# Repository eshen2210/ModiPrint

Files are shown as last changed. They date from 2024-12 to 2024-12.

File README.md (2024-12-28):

# ModiPrint-Desktop

## Introduction

ModiPrint is a powerful, modular, feature-rich open-source 3D bioprinter.


**High resolution Hydrogel Extrusion** 
100 micron alginate filaments (500 micron scale bars).


**Multi-Material prints** 
Printheads mounted on independent Z-actuators enable multiple materials in one print.


**CAD Integration** 
Integration with g-code allows complex 3D models to be fully realized in print.


**Gentle** 
Human induced pluripotent stem cells remained viable for 30 days after print.


**Concentration Gradients** 
Integration of extrusion and inkjet printing embeds small molecule gradients of into hydrogels of any geometry.


## User Guide

This is the complete guide to building and operating ModiPrint. Construction and operation of this 
bioprinter requires the user to: 
1. Acquire all hardware via vendors. 
2. Assemble the hardware using this guide.
3. Install the open-source desktop and microcontroller software. 

Please see the [User Guide](https://github.com/eshen2210/ModiPrint/blob/main/User%20Guide.pdf) for full instructions.

See the [peer-reviewed scientific publication of ModiPrint](https://www.sciencedirect.com/science/article/pii/S2405886620300403).

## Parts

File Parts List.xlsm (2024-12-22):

 |  |  |  | Parts Total (Not Including Tools and Consumables) |  |  |  | Tools |  |  |  | Consumables
 |  |  |  |  | Quantity
Number of Pneumatic Extruders | 1 |  |  | Part Name | (Rounded) | Price ($) Per Unit | Comments | Part Name | Comments |  |  | Part Name | Quantity | Price ($) Per Unit | Comments
 |  |  |  | 062 MINSTAC Adapter – 125/156 MINSTAC | 1 | $52.26 | The Lee Company Quote #TMDA3203950Z – PEEK | Metric Hex Wrenches | For most of the Openbuilds parts. |  |  | 3 cc Syringe Barrels (50 Pack) |  | $30.61 | Nordson EFD Quote #7012072
Number of Microdispensing Inkjets | 1 |  |  | 062 MINSTAC Male – 062 MINSTAC Male | 1 | $12.00 | The Lee Company Quote #TMUA3205950Z – PEEK | Heat Gun (https://www.amazon.com/Genesis-GHG1500A-Temperature-Nozzle-Attachments/dp/B00EU2T8GG) | For the heat shrink. |  |  | 3cc Syringe Barrel Piston (50 Pack) |  | $29.14 | Nordson EFD Quote #7014602
 |  |  |  | 1/4" x 8mm Flexible Coupling | 3 | $6.99 |  | Flat Head Screwdriver |  |  |  | Nordson EFD Tips (https://azcscxpprodcdn.azureedge.net/-/media/Files/Nordson/efd/Products/Data-Sheets/Components/EN_Nordson_EFD_Optimum_Brochure.pdf?la=en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)
 |  |  |  | 10-32 UNF Plug (SPG-10-1/4) (25 Pack) (https://www.pneumadyne.com/plug-fittings-p-2173.html?cPath=135_153_160&ref_id=2178) | 1 | $14.50 |  | Soldering Iron & Solder (https://www.amazon.com/Soldering-Iron-Kit-Temperature-Rarlight/dp/B07PDK3MX1) | For soldering spliced wires. |  |  | Replacement O-Rings for Nordson EFD Adapters (10 Pack) |  | $6.34 | Nordson EFD Quote #7018502
Press Ctrl + Alt + F9 to refresh all part totals after changing printhead counts. |  |  |  | 12 Gauge Wire (https://www.amazon.com/BNTECHGO-Silicone-Flexible-Strands-Stranded/dp/B01ABOPMEI) | 1 | $12.98 |  | Wire Stripper (https://www.amazon.com/Seikotools-Stripper-Yellow-Black-Stripping-Multi-Function/dp/B07KF7D51T) | For splicing wires. |  |  | Replacement O-Rings for Quick Disconnect Fittings (100 Pack) |  | $64.24 | Cole-Parmer Quote #00080XG
Decimal part amounts indicate that only partial packs of parts will be used. |  |  |  | 125/156 MINSTAC – Female Tube – Luer Adapter | 1 | $76.85 | The Lee Company Quote #TMRA9502950Z – PEEK | Power Tool (https://www.amazon.com/BLACK-DECKER-BDCD8C-Lithium-Drill/dp/B0111N8O6G) | For self-tapping screws and to widening the mini gantry plate hole
The "Parts Total" section sums all parts required to build a printer with the specified number of printheads. |  |  |  | 15x20mm Drag Chain (https://www.amazon.com/gp/product/B075FCG31X/ref=ppx_yo_dt_b_search_asin_title?ie=UTF8&psc=1) | 4 | $14.00 |  | 5mm Drill Bit (https://www.amazon.com/Silverline-Cobalt-Drill-Bits-5-0mm/dp/B000LFY1HW) | For widening the mini gantry plate hole
Please report any mistakes to eshen2210@gmail.com |  |  |  | 2 Hole Joining Strip Plate (https://openbuildspartstore.com/2-hole-joining-strip-plate/) | 3 | $1.99 |  | Screw Extractor (https://www.amazon.com/Extractor-Stripped-HassleFree-Hardness-63-65hrc/dp/B07GZ17QD9) | In case the aluminum screws are stripped
Total Cost | $3123.67 |  |  | 24 Gauge Wire (https://www.amazon.com/gp/product/B01KQ0D3M0) | 3 | $14.99 | The quantity here is an estimate.
 |  |  |  | 24V 1A Power Supply (https://www.amazon.com/Signcomplex-Transformers-Switching-Household-Electronics/dp/B0797MW8J6) | 1 | $14.99 | Only necessary if you are using pneumatic extruders.
 |  |  |  | 3 Hole Joining Strip Plate (https://openbuildspartstore.com/3-hole-joining-strip-plate/) | 23 | $1.99
 |  |  |  | 3/16 Barb to 1/4 NPT (25 Pack) (https://www.pneumadyne.com/316-tube-barb-straight-connectors-npt-p-1899.html?cPath=135_136_137_144) | 1 | $7.70
 |  |  |  | 3/16 Barb to 1/8 NPT (EB-1/8) (25 Pack) (https://www.pneumadyne.com/316-tube-barb-straight-connectors-npt-p-1857.html?cPath=135_136_137_142) | 1 | $39.50
 |  |  |  | 3/16 Barb to 10-32 UNF (25 Pack) (https://www.pneumadyne.com/316-tube-barb-straight-connectors-unf-p-1803.html?cPath=135_136_137_138) | 1 | $15.00
 |  |  |  | 3/16'' ID Barb to 1/8'' NPT Female (https://www.amazon.com/Parker-Hannifin-Par-Barb-Connector-Fitting/dp/B01BYLM3T4) | 1 | $10.54
 |  |  |  | 3/16'' ID Quick Disconnect Female (https://www.coleparmer.com/i/cpc-colder-pmcd1703-hose-barb-fitting-body-valved-3-16-tube-id-1-8-flow-size-acetal/0636022) | 2 | $9.90
 |  |  |  | 3/16'' ID Quick Disconnect Male (https://www.coleparmer.com/i/cpc-colder-pmc2203-hose-barb-insert-straight-through-3-16-tube-id-1-8-flow-size-acetal/0636044) | 1 | $3.10
 |  |  |  | 3/16'' ID Tee Connector (10 Pack) (https://www.coleparmer.com/i/cole-parmer-barbed-tee-connector-polyethylene-3-16-10-pack/3062367) | 1 | $17.80
 |  |  |  | 3/16'' ID Tubing (https://www.amazon.com/ATP-Vinyl-Flex-Plastic-Tubing-Length/dp/B00E6BCXQ8) | 1 | $11.68
 |  |  |  | 3/2 Solenoid Valve (McMaster Carr 61975K244) (https://www.mcmaster.com/) | 1 | $58.90
 |  |  |  | 3cc Syringe barrel Adapter with Filter Trap | 1 | $33.22 | Nordson EFD Quote #7012063
 |  |  |  | 5mm * 8mm Flexible Coupling (https://openbuildspartstore.com/5mm-8mm-flexible-coupling/) | 2 | $6.99
 |  |  |  | 7-12V 1A Power Supply (https://www.amazon.com/IBERLS-Adapter-Arduino-Supply-Connectors/dp/B077ZPGQ1K) | 1 | $8.97
 |  |  |  | 8mm Metric Acme Lead Screw (290 mm) (https://openbuildspartstore.com/8mm-metric-acme-lead-screw/) | 2 | $10.99
 |  |  |  | 8mm Metric Acme Lead Screw (540 mm) (https://openbuildspartstore.com/8mm-metric-acme-lead-screw/) | 3 | $21.99
 |  |  |  | Aluminum Spacer (10 Pack) (1.5 inches) (https://openbuildspartstore.com/aluminum-spacers-10-pack/) | 1 | $6.49
 |  |  |  | Aluminum Spacers (10 Pack) (20 mm) (https://openbuildspartstore.com/aluminum-spacers-10-pack/) | 3 | $4.99
 |  |  |  | Aluminum Spacers (10 Pack) (3 mm) (https://openbuildspartstore.com/aluminum-spacers-10-pack/) | 2 | $2.49
 |  |  |  | Aluminum Spacers (10 Pack) (40 mm) (https://openbuildspartstore.com/aluminum-spacers-10-pack/) | 1 | $6.49
 |  |  |  | Aluminum Spacers (10 Pack) (6 mm) (https://openbuildspartstore.com/aluminum-spacers-10-pack/) | 4 | $2.99
 |  |  |  | Aluminum Spacers (10 Pack) (9 mm) (https://openbuildspartstore.com/aluminum-spacers-10-pack/) | 3 | $3.49
 |  |  |  | Anti-Backlash Nut Block for 8mm Metric Acme Lead Screw (https://openbuildspartstore.com/anti-backlash-nut-block-for-8mm-metric-acme-lead-screw/) | 8 | $9.99 | See the link for proper installation instructions.
 |  |  |  | Arduino MEGA (https://www.amazon.com/ELEGOO-ATmega2560-ATMEGA16U2-Projects-Compliant/dp/B01H4ZLZLQ) | 1 | $14.99
 |  |  |  | Ball Bearing 688Z 8x16x5 | 10 | $0.99
 |  |  |  | Black Angle Corner Connector (https://openbuildspartstore.com/black-angle-corner-connector/) | 28 | $2.99
 |  |  |  | Bottom Surface (440 x 500 mm) (https://www.lowes.com/pd/OPTIX-18-in-x-24-in-Clear-Acrylic-Sheet/3502292) | 1 | $26.48 | This is just a big surface for the electronics and has no real requirements. We use acrylic because it's sturdy and can be cut to order in many hardware stores.
 |  |  |  | Braided Cable 1/4'' (~20 ft) (https://www.amazon.com/gp/product/B01M3SG5P7) | 0 | $9.99
 |  |  |  | Button Head Screws M3 (10 Pack) (8mm) (https://openbuildspartstore.com/button-head-screws-m3-25-pack/) | 1 | $1.95
 |  |  |  | C-Beam® End Mount (https://openbuildspartstore.com/c-beam-end-mount/) | 6 | $8.99
 |  |  |  | C-Beam® Linear Rail (500 mm) (https://openbuildspartstore.com/c-beam-linear-rail/) | 3 | $14.99
 |  |  |  | Digital Pressure Gauge (1/8'' NPT) (https://www.amazon.com/Kodiak-Controls-KCDG154145-Pressure-0-145PSI/dp/B00H9ZWPY8) | 1 | $31.99
 |  |  |  | DQ542MA Stepper Motor Driver (https://openbuildspartstore.com/dq542ma-stepper-motor-driver/) | 5 | $39.99
 |  |  |  | Eccentric Spacer (6 mm) (https://openbuildspartstore.com/eccentric-spacer/) | 16 | $1.99 | See the link for proper installation instructions.
 |  |  |  | End Cap (http://openbuildspartstore.com/end-cap/) | 34 | $1.85
 |  |  |  | Heat Shrink (https://www.amazon.com/gp/product/B075WR9FVL) | 1 | $7.98
 |  |  |  | IRF520 MOSFET Driver (5 Pack) (https://www.amazon.com/HiLetgo-IRF520-MOSFET-Arduino-Raspberry/dp/B01I1J14MO/) | 1 | $5.99
 |  |  |  | L Bracket (Double) (http://openbuildspartstore.com/l-bracket/) | 8 | $1.49
 |  |  |  | L Bracket (Single) (https://openbuildspartstore.com/l-bracket/) | 1 | $1.29
 |  |  |  | LM2596 Adjustable Converter (https://www.amazon.com/gp/product/B074XRYC1M/) | 1 | $9.99
 |  |  |  | Lock Collar (https://openbuildspartstore.com/lock-collar/) | 10 | $0.99
 |  |  |  | Low Profile Screws M5 (10 Pack) (10 mm) (https://openbuildspartstore.com/low-profile-screws-m5-10-pack/) | 3 | $1.49
 |  |  |  | Low Profile Screws M5 (10 Pack) (12 mm) (https://openbuildspartstore.com/low-profile-screws-m5-10-pack/) | 1 | $1.49
 |  |  |  | Low Profile Screws M5 (10 Pack) (15 mm) (https://openbuildspartstore.com/low-profile-screws-m5-10-pack/) | 1 | $1.59
 |  |  |  | Low Profile Screws M5 (10 Pack) (20 mm) (https://openbuildspartstore.com/low-profile-screws-m5-10-pack/) | 4 | $1.69
 |  |  |  | Low Profile Screws M5 (10 Pack) (25 mm) (https://openbuildspartstore.com/low-profile-screws-m5-10-pack/) | 1 | $1.79
 |  |  |  | Low Profile Screws M5 (10 Pack) (30 mm) (https://openbuildspartstore.com/low-profile-screws-m5-10-pack/) | 1 | $1.89
 |  |  |  | Low Profile Screws M5 (10 Pack) (35 mm) (https://openbuildspartstore.com/low-profile-screws-m5-10-pack/) | 1 | $1.99
 |  |  |  | Low Profile Screws M5 (10 Pack) (45 mm) (https://openbuildspartstore.com/low-profile-screws-m5-10-pack/) | 1 | $2.19
 |  |  |  | Low Profile Screws M5 (10 Pack) (55 mm) (https://openbuildspartstore.com/low-profile-screws-m5-10-pack/) | 1 | $2.39
 |  |  |  | Low Profile Screws M5 (10 Pack) (60 mm) (https://openbuildspartstore.com/low-profile-screws-m5-10-pack/) | 2 | $2.49
 |  |  |  | Low Profile Screws M5 (10 Pack) (8 mm) (https://openbuildspartstore.com/low-profile-screws-m5-10-pack/) | 9 | $1.39
 |  |  |  | M3 30 mm Screw (20 Pack) (https://www.amazon.com/gp/product/B07DDG19KG) | 1 | $7.99
 |  |  |  | M3 3mm Female Hex Thread Metal Nut (https://www.amazon.com/100Pcs-Female-Thread-Fastener-Silver/dp/B00GYS1SXU) | 1 | $3.69
 |  |  |  | M3 60mm Hex Socket Head Screw (60 Pack) (https://www.amazon.com/Stainless-Steel-Phillips-Screws-60pcs/dp/B012TE19QS) | 1 | $13.59
 |  |  |  | M3 Drop-In Tee Nuts (https://www.amazon.com/CNBTR-10x6x4mm-Aluminum-European-HeadDrop/dp/B01D83GZ7C) | 1 | $7.50
 |  |  |  | M5 1mm Washer (100 Pack) (https://www.amazon.com/Steel-Washer-Plated-Finish-Metric/dp/B009OK4TZO?s=gateway) | 1 | $3.21
 |  |  |  | M5 Drop-In Tee Nuts (https://www.amazon.com/100Pcs-T-Nuts-Carbon-Nickel-Plated-Sliding/dp/B07KSFB7BG?s=gateway) | 1 | $9.99
 |  |  |  | Meanwell LRS-350-24 Power Supply (https://www.amazon.com/MeanWell-LRS-350-24-Power-Supply-350W/dp/B077B36KPB) | 1 | $33.25
 |  |  |  | Micro Limit Switch Kit (https://openbuildspartstore.com/micro-limit-switch-kit/) | 10 | $4.99 | Determines the range limits of the actuator. The location of installation in the Sketchup file is only approximate. Adjust your own limit switch position to tune how far you want your actuator to travel.
 |  |  |  | Microdispensing Valve | 1 | $275.65 | The Lee Company Quote #INKX0507900A
 |  |  |  | Mini Pressure Regulator (McMaster Carr 9172K18) (https://www.mcmaster.com/) | 2 | $37.50
 |  |  |  | Mini V Gantry Plate (http://openbuildspartstore.com/mini-v-gantry-plate/) | 4 | $8.99
 |  |  |  | NEMA 23 Stepper Motor - High Torque Series (http://openbuildspartstore.com/nema-23-stepper-motor-high-torque-series/) | 3 | $39.95
 |  |  |  | Microdispensing Valve Nozzle | 1 | $44.92 | The Lee Company Quote #INZA6542460K
 |  |  |  | Nylon Insert Hex Locknut - M5 (10 Pack) (https://openbuildspartstore.com/nylon-insert-hex-locknut-m5-10-pack/) | 1 | $0.99
 |  |  |  | Pressure Regulator Mounting Bracket (McMaster Carr 9172K24) (https://www.mcmaster.com/9172k24) | 2 | $12.08
 |  |  |  | Pressure Splitter (M32-6) (https://www.pneumadyne.com/station-npt-input-aluminum-manifold-p-2601.html?cPath=193_194_199) | 2 | $10.95
 |  |  |  | Print Surface (440 x 500 mm) (https://www.lowes.com/pd/Gardner-Glass-Products-18-in-x-24-in-Clear-Glass/3121155) | 1 | $9.98 | This is your print surface and should be very stiff to not flex during operation. We use glass for the stiffness and aesthetics but it can be anything you want. You should be able find this stuff cut to order at your local hardware store. It's recommended that you tape off the edges if you decide to use glass.
 |  |  |  | Self Tapping Screw (http://openbuildspartstore.com/self-tapping-screw/) | 46 | $0.29
 |  |  |  | Shim - 12 x 8 x 1mm | 10 | $0.29
 |  |  |  | Slot Washer - 15x5x2mm (https://openbuildspartstore.com/slot-washer-15x5x2mm/) | 16 | $0.19
 |  |  |  | Socket Head Cap Screw M4 (https://openbuildspartstore.com/socket-head-cap-screw-m4/) | 2 | $0.09
 |  |  |  | Standard ROJ Power Cord (https://www.amazon.com/gp/product/B00I0VL96U) | 1 | $7.25
 |  |  |  | Stepper Motor - 68 oz. in (400 steps/rev) (https://www.sparkfun.com/products/10846) | 2 | $17.95
 |  |  |  | Surge Protector (https://www.amazon.com/AmazonBasics-6-Outlet-Protector-2-Pack-2-Foot/dp/B00TP1BWMK?s=gateway) | 1 | $8.45 | This is going to seem really jank, but I recommend securing this with some sturdy 2 sided tape. https://www.amazon.com/Double-Sided-Automotive-Mounting%EF%BC%8CWeatherproof-Decorative-Strip%EF%BC%8CPhoto/dp/B07K2RSJ8D?s=gateway
 |  |  |  | Tee Nuts - M5 (10 Pack) (https://openbuildspartstore.com/tee-nuts-m5-10-pack/) | 10 | $2.99 | See Drop In Tee Nuts as an easier to use alternative https://www.amazon.com/100Pcs-T-Nuts-Carbon-Nickel-Plated-Sliding/dp/B07KSFB7BG?s=gateway
 |  |  |  | Threaded Rod Plate - NEMA 17 Stepper Motor (http://openbuildspartstore.com/threaded-rod-plate-nema-17-stepper-motor/) | 4 | $6.99
 |  |  |  | Turn Key Hose Clamp 5/8'' to 1-1/4'' (10 Pack) (https://www.amazon.com/gp/product/B006IOZ2TG/ref=oh_aui_detailpage_o08_s00?ie=UTF8&psc=1) | 1 | $12.39
 |  |  |  | Vacuum Regulator (McMaster Carr 41585K43) (https://www.mcmaster.com/41585k43) | 1 | $56.70
 |  |  |  | Valve Driver | 1 | $174.80 | The Lee Company Quote #IECX0501350A
 |  |  |  | V-Slot Linear Rail 20mm x 20mm (250mm) (http://openbuildspartstore.com/v-slot-20x20-linear-rail/) | 2 | $3.29
 |  |  |  | V-Slot Linear Rail 20mm x 40mm (250mm) (http://openbuildspartstore.com/v-slot-20x40-linear-rail/) | 2 | $3.99
 |  |  |  | V-Slot® 20x20 Linear Rail (500 mm) (https://openbuildspartstore.com/v-slot-20x20-linear-rail/) | 4 | $5.49
 |  |  |  | V-Slot® 20x40 Linear Rail (250 mm) (https://openbuildspartstore.com/v-slot-20x40-linear-rail/) | 1 | $3.99
 |  |  |  | V-Slot® 20x40 Linear Rail (500 mm) (https://openbuildspartstore.com/v-slot-20x40-linear-rail/) | 2 | $6.99
 |  |  |  | V-Slot® 20x80 Linear Rail (250mm) (http://openbuildspartstore.com/v-slot-20x80-linear-rail/) | 3 | $5.99
 |  |  |  | V-Slot® 20x80 Linear Rail (500 mm) (https://openbuildspartstore.com/v-slot-20x80-linear-rail/) | 1 | $10.99
 |  |  |  | XLarge C-Beam Gantry Plate (https://openbuildspartstore.com/xlarge-c-beam-gantry-plate/) | 6 | $14.99
 |  |  |  | Xtreme Mini V Wheel Kit (https://openbuildspartstore.com/xtreme-mini-v-wheel-kit/) | 8 | $5.99
 |  |  |  | Xtreme Solid V Wheel Kit (https://openbuildspartstore.com/xtreme-solid-v-wheel-kit/) | 24 | $6.99 | Also comes with nuts and shims that will be used in conjunction with the wheel. A shim must be sandwiched in between 2 ball bearings within each wheel.
 |  |  |  | For Sterile Prints
 |  |  |  | Autoclavable 3/16'' ID Tubing (https://www.amazon.com/gp/product/B004VHJRCA) | 1 | $29.83
 |  |  |  | Autoclavable In-Line HEPA Filter (https://www.coleparmer.com/i/whatman-6723-5000-hepa-vent-filters-10pk-50mm-dia/2970090) | 1 | $122.00
 |  |  |  | Total |  | $3123.67
2 Y Actuators |  |  |  | Frame & Print Surface |  |  |  | Y Drag Chain & Outlet Extension |  |  |  | X Actuator
Part Name | Quantity | Price ($) Per Unit | Comments | Part Name | Quantity | Price ($) Per Unit | Comments | Part Name | Quantity | Price ($) Per Unit | Comments | Part Name | Quantity | Price ($) Per Unit | Comments
1/4" x 8mm Flexible Coupling | 2 | $6.99 |  | 2 Hole Joining Strip Plate (https://openbuildspartstore.com/2-hole-joining-strip-plate/) | 2 | $1.99 |  | 15x20mm Drag Chain (https://www.amazon.com/gp/product/B075FCG31X/ref=ppx_yo_dt_b_search_asin_title?ie=UTF8&psc=1) | 2 | $14.00 |  | 1/4" x 8mm Flexible Coupling | 1 | $6.99
3 Hole Joining Strip Plate (https://openbuildspartstore.com/3-hole-joining-strip-plate/) | 2 | $1.99 |  | 3 Hole Joining Strip Plate (https://openbuildspartstore.com/3-hole-joining-strip-plate/) | 6 | $1.99 |  | 3 Hole Joining Strip Plate (https://openbuildspartstore.com/3-hole-joining-strip-plate/) | 5 | $1.99 |  | 8mm Metric Acme Lead Screw (540 mm) (https://openbuildspartstore.com/8mm-metric-acme-lead-screw/) | 1 | $21.99
8mm Metric Acme Lead Screw (540 mm) (https://openbuildspartstore.com/8mm-metric-acme-lead-screw/) | 2 | $21.99 |  | Black Angle Corner Connector (https://openbuildspartstore.com/black-angle-corner-connector/) | 12 | $2.99 |  | Aluminum Spacers (10 Pack) (20 mm) (https://openbuildspartstore.com/aluminum-spacers-10-pack/) | 0.3 | $4.99 |  | Aluminum Spacers (10 Pack) (20 mm) (https://openbuildspartstore.com/aluminum-spacers-10-pack/) | 0.8 | $4.99
Aluminum Spacers (10 Pack) (20 mm) (https://openbuildspartstore.com/aluminum-spacers-10-pack/) | 0.8 | $4.99 |  | Bottom Surface (440 x 500 mm) (https://www.lowes.com/pd/OPTIX-18-in-x-24-in-Clear-Acrylic-Sheet/3502292) | 1 | $26.48 | This is just a big surface for the electronics and has no real requirements. We use acrylic because it's sturdy and can be cut to order in many hardware stores. | Aluminum Spacers (10 Pack) (6 mm) (https://openbuildspartstore.com/aluminum-spacers-10-pack/) | 0.1 | $2.99 |  | Aluminum Spacers (10 Pack) (3 mm) (https://openbuildspartstore.com/aluminum-spacers-10-pack/) | 0.4 | $2.49
Aluminum Spacers (10 Pack) (3 mm) (https://openbuildspartstore.com/aluminum-spacers-10-pack/) | 0.8 | $2.49 |  | End Cap (http://openbuildspartstore.com/end-cap/) | 4 | $1.85 |  | End Cap (http://openbuildspartstore.com/end-cap/) | 8 | $1.85 |  | Aluminum Spacers (10 Pack) (40 mm) (https://openbuildspartstore.com/aluminum-spacers-10-pack/) | 0.2 | $6.49
Aluminum Spacers (10 Pack) (40 mm) (https://openbuildspartstore.com/aluminum-spacers-10-pack/) | 0.4 | $6.49 |  | Low Profile Screws M5 (10 Pack) (8 mm) (https://openbuildspartstore.com/low-profile-screws-m5-10-pack/) | 4.2 | $1.39 |  | L Bracket (Single) (https://openbuildspartstore.com/l-bracket/) | 1 | $1.29 |  | Aluminum Spacers (10 Pack) (6 mm) (https://openbuildspartstore.com/aluminum-spacers-10-pack/) | 0.4 | $2.99
Aluminum Spacers (10 Pack) (6 mm) (https://openbuildspartstore.com/aluminum-spacers-10-pack/) | 1 | $2.99 |  | Self Tapping Screw (http://openbuildspartstore.com/self-tapping-screw/) | 8 | $0.29 |  | Low Profile Screws M5 (10 Pack) (10 mm) (https://openbuildspartstore.com/low-profile-screws-m5-10-pack/) | 0.1 | $1.49 |  | Aluminum Spacers (10 Pack) (9 mm) (https://openbuildspartstore.com/aluminum-spacers-10-pack/) | 0.4 | $3.49
Aluminum Spacers (10 Pack) (9 mm) (https://openbuildspartstore.com/aluminum-spacers-10-pack/) | 0.8 | $3.49 |  | Tee Nuts - M5 (10 Pack) (https://openbuildspartstore.com/tee-nuts-m5-10-pack/) | 4.2 | $2.99 | See Drop In Tee Nuts as an easier to use alternative https://openbuildspartstore.com/drop-in-tee-nuts/ | Low Profile Screws M5 (10 Pack) (12 mm) (https://openbuildspartstore.com/low-profile-screws-m5-10-pack/) | 0.1 | $1.49 |  | Anti-Backlash Nut Block for 8mm Metric Acme Lead Screw (https://openbuildspartstore.com/anti-backlash-nut-block-for-8mm-metric-acme-lead-screw/) | 2 | $9.99 | See the link for proper installation instructions.
Anti-Backlash Nut Block for 8mm Metric Acme Lead Screw (https://openbuildspartstore.com/anti-backlash-nut-block-for-8mm-metric-acme-lead-screw/) | 4 | $9.99 | See the link for proper installation instructions. | Print Surface (440 x 500 mm) (https://www.lowes.com/pd/Gardner-Glass-Products-18-in-x-24-in-Clear-Glass/3121155) | 1 | $9.98 | This is your print surface and should be very stiff to not flex during operation. We use glass for the stiffness and aesthetics but it can be anything you want. You should be able find this stuff cut to order at your local hardware store. It's recommended that you tape off the edges if you decide to use glass. | Low Profile Screws M5 (10 Pack) (30 mm) (https://openbuildspartstore.com/low-profile-screws-m5-10-pack/) | 0.2 | $1.89 |  | Ball Bearing 688Z 8x16x5 | 2 | $0.99
Ball Bearing 688Z 8x16x5 | 4 | $0.99 |  | V-Slot® 20x20 Linear Rail (500 mm) (https://openbuildspartstore.com/v-slot-20x20-linear-rail/) | 4 | $5.49 |  | Low Profile Screws M5 (10 Pack) (35 mm) (https://openbuildspartstore.com/low-profile-screws-m5-10-pack/) | 0.1 | $1.99 |  | C-Beam® End Mount (https://openbuildspartstore.com/c-beam-end-mount/) | 2 | $8.99
Black Angle Corner Connector (https://openbuildspartstore.com/black-angle-corner-connector/) | 2 | $2.99 |  | V-Slot® 20x40 Linear Rail (250 mm) (https://openbuildspartstore.com/v-slot-20x40-linear-rail/) | 1 | $3.99 |  | Low Profile Screws M5 (10 Pack) (8 mm) (https://openbuildspartstore.com/low-profile-screws-m5-10-pack/) | 0.6 | $1.39 |  | C-Beam® Linear Rail (500 mm) (https://openbuildspartstore.com/c-beam-linear-rail/) | 1 | $14.99
C-Beam® End Mount (https://openbuildspartstore.com/c-beam-end-mount/) | 4 | $8.99 |  | V-Slot® 20x40 Linear Rail (500 mm) (https://openbuildspartstore.com/v-slot-20x40-linear-rail/) | 1 | $6.99 |  | M5 Drop-In Tee Nuts (https://www.amazon.com/100Pcs-T-Nuts-Carbon-Nickel-Plated-Sliding/dp/B07KSFB7BG?s=gateway) | 0.09 | $9.99 |  | DQ542MA Stepper Motor Driver (https://openbuildspartstore.com/dq542ma-stepper-motor-driver/) | 1 | $39.99
C-Beam® Linear Rail (500 mm) (https://openbuildspartstore.com/c-beam-linear-rail/) | 2 | $14.99 |  |  |  |  |  | Nylon Insert Hex Locknut - M5 (10 Pack) (https://openbuildspartstore.com/nylon-insert-hex-locknut-m5-10-pack/) | 0.2 | $0.99 |  | Eccentric Spacer (6 mm) (https://openbuildspartstore.com/eccentric-spacer/) | 4 | $1.99 | See the link for proper installation instructions.
DQ542MA Stepper Motor Driver (https://openbuildspartstore.com/dq542ma-stepper-motor-driver/) | 2 | $39.99 |  |  |  |  |  | M5 1mm Washer (100 Pack) (https://www.amazon.com/Steel-Washer-Plated-Finish-Metric/dp/B009OK4TZO?s=gateway) | 0.04 | $3.21 |  | End Cap (http://openbuildspartstore.com/end-cap/) | 8 | $1.85
Eccentric Spacer (6 mm) (https://openbuildspartstore.com/eccentric-spacer/) | 8 | $1.99 | See the link for proper installation instructions. |  |  |  |  | Self Tapping Screw (http://openbuildspartstore.com/self-tapping-screw/) | 8 | $0.29 |  | Lock Collar (https://openbuildspartstore.com/lock-collar/) | 2 | $0.99
End Cap (http://openbuildspartstore.com/end-cap/) | 8 | $1.85 |  |  |  |  |  | Surge Protector (https://www.amazon.com/AmazonBasics-6-Outlet-Protector-2-Pack-2-Foot/dp/B00TP1BWMK?s=gateway) | 1 | $8.45 | This is going to seem really jank, but I recommend securing this with some sturdy 2 sided tape. https://www.amazon.com/Double-Sided-Automotive-Mounting%EF%BC%8CWeatherproof-Decorative-Strip%EF%BC%8CPhoto/dp/B07K2RSJ8D?s=gateway | Low Profile Screws M5 (10 Pack) (10 mm) (https://openbuildspartstore.com/low-profile-screws-m5-10-pack/) | 0.4 | $1.49
L Bracket (Double) (http://openbuildspartstore.com/l-bracket/) | 2 | $1.49 |  |  |  |  |  | V-Slot® 20x80 Linear Rail (500 mm) (https://openbuildspartstore.com/v-slot-20x80-linear-rail/) | 1 | $10.99 |  | Low Profile Screws M5 (10 Pack) (20 mm) (https://openbuildspartstore.com/low-profile-screws-m5-10-pack/) | 1.2 | $1.69
Lock Collar (https://openbuildspartstore.com/lock-collar/) | 4 | $0.99 |  |  |  |  |  |  |  |  |  | Low Profile Screws M5 (10 Pack) (55 mm) (https://openbuildspartstore.com/low-profile-screws-m5-10-pack/) | 0.2 | $2.39
Low Profile Screws M5 (10 Pack) (10 mm) (https://openbuildspartstore.com/low-profile-screws-m5-10-pack/) | 0.8 | $1.49 |  |  |  |  |  |  |  |  |  | Low Profile Screws M5 (10 Pack) (60 mm) (https://openbuildspartstore.com/low-profile-screws-m5-10-pack/) | 0.8 | $2.49
Low Profile Screws M5 (10 Pack) (20 mm) (https://openbuildspartstore.com/low-profile-screws-m5-10-pack/) | 2.4 | $1.69 |  |  |  |  |  |  |  |  |  | Micro Limit Switch Kit (https://openbuildspartstore.com/micro-limit-switch-kit/) | 2 | $4.99 | Determines the range limits of the actuator. The location of installation in the Sketchup file is only approximate. Adjust your own limit switch position to tune how far you want your actuator to travel.
Low Profile Screws M5 (10 Pack) (55 mm) (https://openbuildspartstore.com/low-profile-screws-m5-10-pack/) | 0.4 | $2.39 |  |  |  |  |  |  |  |  |  | NEMA 23 Stepper Motor - High Torque Series (http://openbuildspartstore.com/nema-23-stepper-motor-high-torque-series/) | 1 | $39.95
Low Profile Screws M5 (10 Pack) (60 mm) (https://openbuildspartstore.com/low-profile-screws-m5-10-pack/) | 1.2 | $2.49 |  |  |  |  |  |  |  |  |  | Self Tapping Screw (http://openbuildspartstore.com/self-tapping-screw/) | 8 | $0.29
Low Profile Screws M5 (10 Pack) (8 mm) (https://openbuildspartstore.com/low-profile-screws-m5-10-pack/) | 1.4 | $1.39 |  |  |  |  |  |  |  |  |  | Shim - 12 x 8 x 1mm | 2 | $0.29
Micro Limit Switch Kit (https://openbuildspartstore.com/micro-limit-switch-kit/) | 4 | $4.99 | Determines the range limits of the actuator. The location of installation in the Sketchup file is only approximate. Adjust your own limit switch position to tune how far you want your actuator to travel. |  |  |  |  |  |  |  |  | Slot Washer - 15x5x2mm (https://openbuildspartstore.com/slot-washer-15x5x2mm/) | 4 | $0.19
NEMA 23 Stepper Motor - High Torque Series (http://openbuildspartstore.com/nema-23-stepper-motor-high-torque-series/) | 2 | $39.95 |  |  |  |  |  |  |  |  |  | Tee Nuts - M5 (10 Pack) (https://openbuildspartstore.com/tee-nuts-m5-10-pack/) | 0.4 | $2.99 | See Drop In Tee Nuts as an easier to use alternative https://www.amazon.com/100Pcs-T-Nuts-Carbon-Nickel-Plated-Sliding/dp/B07KSFB7BG?s=gateway
Self Tapping Screw (http://openbuildspartstore.com/self-tapping-screw/) | 10 | $0.29 |  |  |  |  |  |  |  |  |  | V-Slot® 20x80 Linear Rail (250mm) (http://openbuildspartstore.com/v-slot-20x80-linear-rail/) | 1 | $5.99
Shim - 12 x 8 x 1mm | 4 | $0.29 |  |  |  |  |  |  |  |  |  | XLarge C-Beam Gantry Plate (https://openbuildspartstore.com/xlarge-c-beam-gantry-plate/) | 2 | $14.99
Slot Washer - 15x5x2mm (https://openbuildspartstore.com/slot-washer-15x5x2mm/) | 12 | $0.19 |  |  |  |  |  |  |  |  |  | Xtreme Solid V Wheel Kit (https://openbuildspartstore.com/xtreme-solid-v-wheel-kit/) | 8 | $6.99 | Also comes with nuts and shims that will be used in conjunction with the wheel. A shim must be sandwiched in between 2 ball bearings within each wheel.
Tee Nuts - M5 (10 Pack) (https://openbuildspartstore.com/tee-nuts-m5-10-pack/) | 2.4 | $2.99 | See Drop In Tee Nuts as an easier to use alternative https://www.amazon.com/100Pcs-T-Nuts-Carbon-Nickel-Plated-Sliding/dp/B07KSFB7BG?s=gateway
V-Slot® 20x80 Linear Rail (250mm) (http://openbuildspartstore.com/v-slot-20x80-linear-rail/) | 2 | $5.99
XLarge C-Beam Gantry Plate (https://openbuildspartstore.com/xlarge-c-beam-gantry-plate/) | 4 | $14.99
Xtreme Solid V Wheel Kit (https://openbuildspartstore.com/xtreme-solid-v-wheel-kit/) | 16 | $6.99 | Also comes with nuts and shims that will be used in conjunction with the wheel. A shim must be sandwiched in between 2 ball bearings within each wheel.
X Drag Chain and Pneumatics Panel |  |  |  | All Z Actuators |  |  |  | All Pneumatic Extruders |  |  |  | All Microdispensing Valves
Part Name | Quantity | Price ($) Per Unit | Comments | Part Name | Quantity | Price ($) Per Unit | Comments | Part Name | Quantity | Price ($) Per Unit | Comments | Part Name | Quantity | Price ($) Per Unit | Comments
10-32 UNF Plug (SPG-10-1/4) (25 Pack) (https://www.pneumadyne.com/plug-fittings-p-2173.html?cPath=135_153_160&ref_id=2178) | 1 | $14.50 |  | 5mm * 8mm Flexible Coupling (https://openbuildspartstore.com/5mm-8mm-flexible-coupling/) | 2 | $6.99
15x20mm Drag Chain (https://www.amazon.com/gp/product/B075FCG31X/ref=ppx_yo_dt_b_search_asin_title?ie=UTF8&psc=1) | 2 | $14.00 |  | 8mm Metric Acme Lead Screw (290 mm) (https://openbuildspartstore.com/8mm-metric-acme-lead-screw/) | 2 | $10.99 |  | Solenoid Valve |  |  |  | Microdispensing Valve
2 Hole Joining Strip Plate (https://openbuildspartstore.com/2-hole-joining-strip-plate/) | 1 | $1.99 |  | Aluminum Spacer (10 Pack) (1.5 inches) (https://openbuildspartstore.com/aluminum-spacers-10-pack/) | 0.6 | $6.49 |  | 3 Hole Joining Strip Plate (https://openbuildspartstore.com/3-hole-joining-strip-plate/) | 2 | $1.99 |  | LM2596 Adjustable Converter (https://www.amazon.com/gp/product/B074XRYC1M/) | 1 | $9.99
3 Hole Joining Strip Plate (https://openbuildspartstore.com/3-hole-joining-strip-plate/) | 2 | $1.99 |  | Aluminum Spacers (10 Pack) (20 mm) (https://openbuildspartstore.com/aluminum-spacers-10-pack/) | 0.4 | $4.99 |  | 3/16 Barb to 10-32 UNF (25 Pack) (https://www.pneumadyne.com/316-tube-barb-straight-connectors-unf-p-1803.html?cPath=135_136_137_138) | 0.12 | $15.00 |  | 062 MINSTAC Adapter – 125/156 MINSTAC | 1 | $52.26 | The Lee Company Quote #TMDA3203950Z – PEEK
3/16 Barb to 1/8 NPT (EB-1/8) (25 Pack) (https://www.pneumadyne.com/316-tube-barb-straight-connectors-npt-p-1857.html?cPath=135_136_137_142) | 1 | $39.50 |  | Aluminum Spacers (10 Pack) (6 mm) (https://openbuildspartstore.com/aluminum-spacers-10-pack/) | 2.2 | $2.99 |  | 3/2 Solenoid Valve (McMaster Carr 61975K244) (https://www.mcmaster.com/) | 1 | $58.90 |  | 062 MINSTAC Male – 062 MINSTAC Male | 1 | $12.00 | The Lee Company Quote #TMUA3205950Z – PEEK
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

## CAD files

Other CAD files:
Sketchup Files/Z Actuator.skp

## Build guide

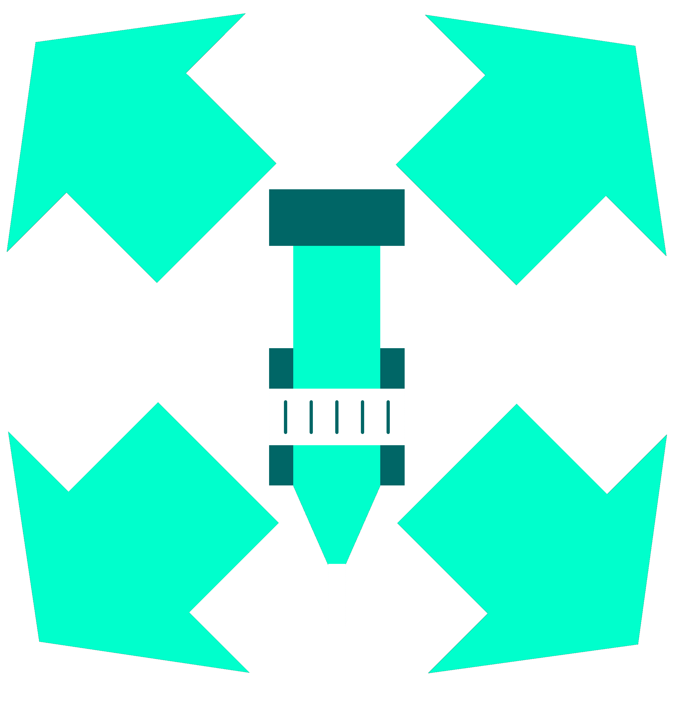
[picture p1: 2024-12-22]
ModiPrint Desktop Code/ModiPrint/Resources/Buttons/SetPrintheadOffset.png

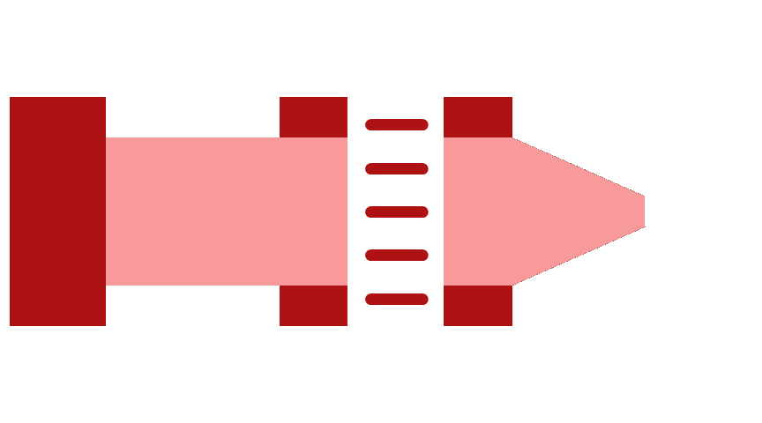
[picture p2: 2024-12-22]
ModiPrint Desktop Code/ModiPrint/Resources/PrintSequenceControl/PrintheadDisabled.png

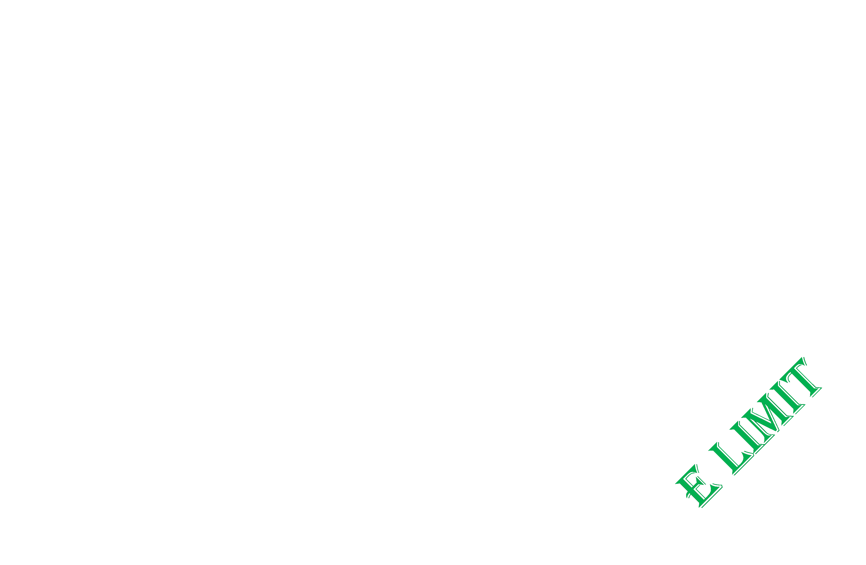
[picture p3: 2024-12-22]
ModiPrint Desktop Code/ModiPrint/Resources/XYZEControl/XYZELimits/ELowerLimit.png

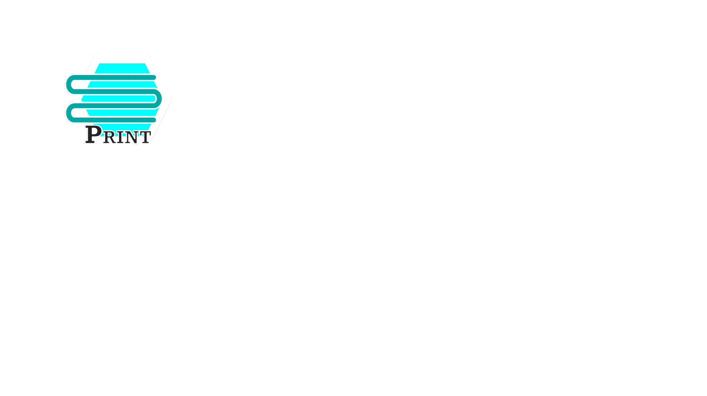
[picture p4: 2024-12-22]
ModiPrint Desktop Code/ModiPrint/Resources/MainWindow/PrintMouseOver.PNG

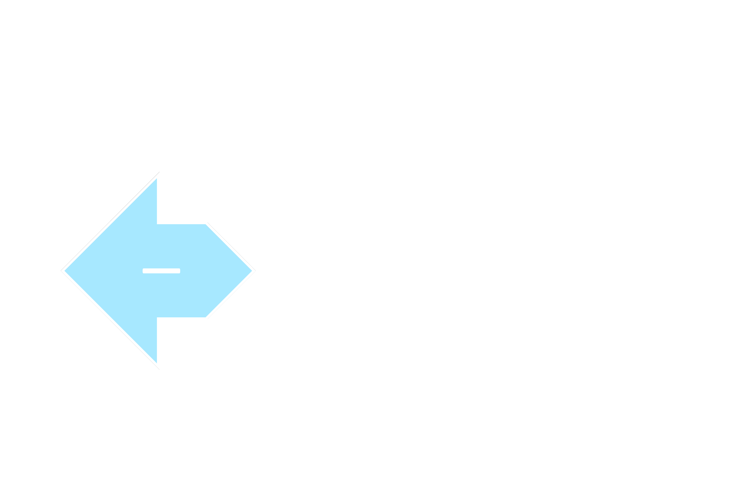
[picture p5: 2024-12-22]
ModiPrint Desktop Code/ModiPrint/Resources/XYZEControl/XMinusMouseOver.PNG

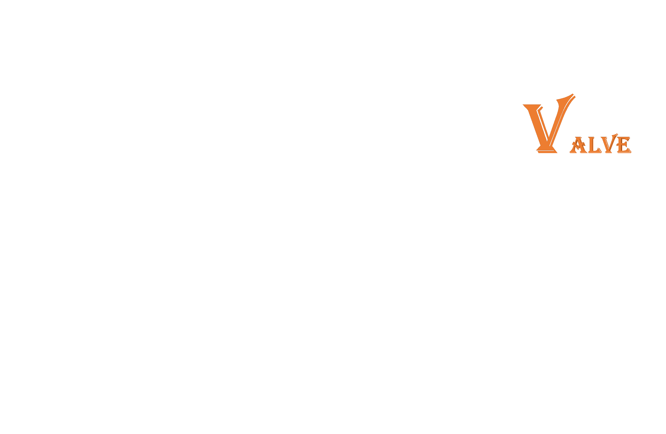
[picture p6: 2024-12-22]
ModiPrint Desktop Code/ModiPrint/Resources/XYZEControl/ValvePrintheadBackground.png

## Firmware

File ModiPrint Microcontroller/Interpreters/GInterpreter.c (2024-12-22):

#include "ModiPrintMicro.h"

void ExecuteG00(char * receiveMessage, uint8_t * receiveIndex)
{
	//Motor movements in relative coordinates.
	int32_t xSteps = 0;
	int32_t ySteps = 0;
	int32_t zSteps = 0;
	float exitSpeed = 0;

	NextChar(receiveMessage, receiveIndex);
	while (IsInterpretLoopTerminated(receiveMessage, *receiveIndex) == FALSE)
	{		
		switch (receiveMessage[*receiveIndex])
		{			
			case 'X':
				xSteps = (int32_t)ParseNextNum(receiveMessage, receiveIndex);
				break;
			case 'Y':
				ySteps = (int32_t)ParseNextNum(receiveMessage, receiveIndex);
				break;
			case 'Z':
				zSteps = (int32_t)ParseNextNum(receiveMessage, receiveIndex);
				break;
			case 'T':
				exitSpeed = ParseNextNum(receiveMessage, receiveIndex);
				break;
			default:
				HandleError(ERROR_SYNTAX_INVALID);
				return;
		}
		NextChar(receiveMessage, receiveIndex);
	}

	OperateMoveXYZ(xSteps, ySteps, zSteps, exitSpeed);
}

void ExecuteG01(char * receiveMessage, uint8_t * receiveIndex)
{
	//Only run if this printer is currently using a motor-driven Printhead.
	if (Hardware.PrintheadType == PT_Motor)
	{
		int32_t printSteps = 0;
		int32_t xSteps = 0;
		int32_t ySteps = 0;
		int32_t zSteps = 0;
		float exitSpeed = 0;

		NextChar(receiveMessage, receiveIndex);
		while (IsInterpretLoopTerminated(receiveMessage, *receiveIndex) == FALSE)
		{
			switch (receiveMessage[*receiveIndex])
			{
				case 'E':
					printSteps = (int32_t)ParseNextNum(receiveMessage, receiveIndex);
					break;
				case 'X':
					xSteps = (int32_t)ParseNextNum(receiveMessage, receiveIndex);
					break;
				case 'Y':
					ySteps = (int32_t)ParseNextNum(receiveMessage, receiveIndex);
					break;
				case 'Z':
					zSteps = (int32_t)ParseNextNum(receiveMessage, receiveIndex);
					break;
				case 'T':
					exitSpeed = ParseNextNum(receiveMessage, receiveIndex);
					break;
				default:
					HandleError(ERROR_SYNTAX_INVALID);
					return;
			}
			NextChar(receiveMessage, receiveIndex);
		}

		OperateMotorPrintWithMovement(printSteps, xSteps, ySteps, zSteps, exitSpeed);
	}
	else
	{
		HandleError(ERROR_HARDWARE_UNSET);
		return;
	}
}

void ExecuteG02(char * receiveMessage, uint8_t * receiveIndex)
{
	if (Hardware.PrintheadType == PT_Valve)
	{
		int32_t xSteps = 0;
		int32_t ySteps = 0;
		int32_t zSteps = 0;
		float exitSpeed = 0;

		NextChar(receiveMessage, receiveIndex);
		while (IsInterpretLoopTerminated(receiveMessage, *receiveIndex) == FALSE)
		{
			switch (receiveMessage[*receiveIndex])
			{
				case 'X':
					xSteps = (int32_t)ParseNextNum(receiveMessage, receiveIndex);
					break;
				case 'Y':
					ySteps = (int32_t)ParseNextNum(receiveMessage, receiveIndex);
					break;
				case 'Z':
					zSteps = (int32_t)ParseNextNum(receiveMessage, receiveIndex);
					break;
				case 'T':
					exitSpeed = ParseNextNum(receiveMessage, receiveIndex);
					break;
				default:
					HandleError(ERROR_SYNTAX_INVALID);
					return;
			}
			NextChar(receiveMessage, receiveIndex);
		}

		OperateValvePrintWithMovement(xSteps, ySteps, zSteps, exitSpeed);
	}
	else
	{
		HandleError(ERROR_HARDWARE_UNSET);
		return;
	}
}

void ExecuteG11(char * receiveMessage, uint8_t * receiveIndex)
{
	if (Hardware.PrintheadType == PT_Motor)
	{
		int32_t printSteps = 0;

		NextChar(receiveMessage, receiveIndex);
		while (IsInterpretLoopTerminated(receiveMessage, *receiveIndex) == FALSE)
		{
			switch (receiveMessage[*receiveIndex])
			{
				case 'E':
					printSteps = (int32_t)ParseNextNum(receiveMessage, receiveIndex);
					break;
				default:
					HandleError(ERROR_SYNTAX_INVALID);
					return;
			}
			NextChar(receiveMessage, receiveIndex);
		}

		OperateMotorPrintWithoutMovement(printSteps);
	}
	else
	{
		HandleError(ERROR_HARDWARE_UNSET);
		return;
	}
}

void ExecuteG12(char * receiveMessage, uint8_t * receiveIndex)
{
	if (Hardware.PrintheadType == PT_Valve)
	{
		NextChar(receiveMessage, receiveIndex);
		while (IsInterpretLoopTerminated(receiveMessage, *receiveIndex) == FALSE)
		{
			switch (receiveMessage[*receiveIndex])
			{
				case 'O':
				{
					uint32_t openTime = (uint32_t)ParseNextNum(receiveMessage, receiveIndex);
					OperateValvePrintWithoutMovement(openTime);
					break;
				}
				case 'C':
				{
					OperateStopValvePrint(&Hardware.ValvePrinthead);
					break;
				}
				default:
				{
					HandleError(ERROR_SYNTAX_INVALID);
					return;
				}
			}
			NextChar(receiveMessage, receiveIndex);
		}
	}
	else
	{
		HandleError(ERROR_HARDWARE_UNSET);
		return;
	}
}

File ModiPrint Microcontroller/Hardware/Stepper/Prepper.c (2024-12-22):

#include "ModiPrintMicro.h"

void PrepareStepperRealTime(movement_t * movement, int32_t xSteps, int32_t ySteps, int32_t zSteps, int32_t eSteps, float movementExitSpeed, uint8_t doValvePrint)
{	
	xyz_stage_t * xyzStage = &Hardware.XYZStage;
	motor_printhead_t * motorPrinthead = &Hardware.MotorPrinthead;
	valve_printhead_t * valvePrinthead = (doValvePrint == TRUE) ? &Hardware.ValvePrinthead : NULL;
	
	//maxSpeed in steps/s.
	//acceleration in steps/s^2.
	//timeSquared in s^2.
	//Some values with "cycles" in its variable name have time in units of Timer 1 cycles.

	movement->MovementExitSpeed = movementExitSpeed;

	//Set the on-movement pin.
	if (valvePrinthead != NULL)
	{
		movement->ValvePin = (IsPinValid(valvePrinthead->ValvePin) == TRUE) ? valvePrinthead->ValvePin : PIN_ID_NULL;
	}
	else
	{
		movement->ValvePin = PIN_ID_NULL;
	}

	//Load the number of steps for each actuator stepper into the data block.
	movement->XTotalSteps = xSteps;
	movement->YTotalSteps = ySteps;
	movement->ZTotalSteps = zSteps;
	movement->ETotalSteps = eSteps;

	//Absolute values for each of the steps.
	uint32_t xAbsTotalSteps = (xSteps >= 0) ? xSteps : (-1 * xSteps);
	uint32_t yAbsTotalSteps = (ySteps >= 0) ? ySteps : (-1 * ySteps);
	uint32_t zAbsTotalSteps = (zSteps >= 0) ? zSteps : (-1 * zSteps);
	uint32_t eAbsTotalSteps = (eSteps >= 0) ? eSteps : (-1 * eSteps);

	//The Bresenham counters should begin at zero.
	movement->XCounter = movement->YCounter = movement->ZCounter = movement->ECounter = 0;

	//Initialize the number of leading steps.
	//Leading is defines the stepper that will take the most steps in this movement.
	//The stepper timer (Timer 1) will tick based on the leading stepper's movement.
	//The other stepper movements will be rasterized with the Bresenham algorithm.
	movement->LeadingStepsTaken = 0;
	movement->LeadingStepsTotal = xAbsTotalSteps;
	movement->LeadingStepsTotal = (yAbsTotalSteps > movement->LeadingStepsTotal) ? yAbsTotalSteps : movement->LeadingStepsTotal;
	movement->LeadingStepsTotal = (zAbsTotalSteps > movement->LeadingStepsTotal) ? zAbsTotalSteps : movement->LeadingStepsTotal;
	movement->LeadingStepsTotal = (eAbsTotalSteps > movement->LeadingStepsTotal) ? eAbsTotalSteps : movement->LeadingStepsTotal;

	//The "distance" of the movement, which is simply the magnitude of this movement.
	//Used to scale the speeds of the movement.
	double movementTotalSteps = 0;
	//Find the max speed and acceleration of this movement such that no acceleration values are exceeded for each Axis.
	float movementMaxSpeed = FLT_MAX;
	float movementAcceleration = FLT_MAX;
	//Set the step pulse duration of all motors (in microseconds).
	//Ideally, each stepper motor would have individualized step pulse durations. However, there isn't enough timers on the Mega 2560 to end four stepper pulses asynchronously.
	//The compromise is that all stepper motors will share the longest minimum pulse duration among all steppers.
	uint16_t stepPulseDuration = 0; //(in microseconds)

	//Calculate movementTotalSteps and stepPulseDuration in these if statements.
	if (xSteps != 0) 
	{ 
		movementTotalSteps = ((float)xSteps * (float)xSteps);
		stepPulseDuration = (stepPulseDuration > xyzStage->XAxis.StepPulseDuration) ? stepPulseDuration : xyzStage->XAxis.StepPulseDuration;
	}
	if (ySteps != 0) 
	{ 
		movementTotalSteps += ((float)ySteps * (float)ySteps);
		stepPulseDuration = (stepPulseDuration > xyzStage->YAxis.StepPulseDuration) ? stepPulseDuration : xyzStage->YAxis.StepPulseDuration;
	}
	if (zSteps != 0)
	{
		movementTotalSteps += ((float)zSteps * (float)zSteps);
		stepPulseDuration = (stepPulseDuration > xyzStage->ZAxis.StepPulseDuration) ? stepPulseDuration : xyzStage->ZAxis.StepPulseDuration;
	}
	if (eSteps != 0)
	{
		movementTotalSteps += ((float)eSteps * (float)eSteps);
		stepPulseDuration = (stepPulseDuration > motorPrinthead->StepPulseDuration) ? stepPulseDuration : motorPrinthead->StepPulseDuration;
	}
	movementTotalSteps = sqrt(movementTotalSteps);
	
	//Calculate the speeds of the leading stepper.
	//Leading speeds are in units of steps/cycles.
	//Leading acceleration is in units of steps/cycles^2.
	float leadingAcceleration = FLT_MAX;
	float leadingMaxSpeed = 0;
	float leadingEntrySpeed = 0;
	float leadingExitSpeed = 0;
	if (xSteps != 0)
	{
		float invXScaled = (float)movementTotalSteps / (float)xAbsTotalSteps;
		movementMaxSpeed = xyzStage->XAxis.MaxSpeed * invXScaled;
		movementAcceleration = xyzStage->XAxis.MaxAcceleration * invXScaled;

		//If the X actuator has the leading stepper...
		if (movement->LeadingStepsTotal == xAbsTotalSteps)
		{
			float xScaled = (float)xAbsTotalSteps / (float)movementTotalSteps;
			leadingAcceleration = movementAcceleration * xScaled;
			leadingMaxSpeed = movementMaxSpeed * xScaled;
			leadingEntrySpeed = movement->MovementEntrySpeed * xScaled;
			leadingExitSpeed = movementExitSpeed * xScaled;
		}
	}
	if (ySteps != 0)
	{
		float invYScaled = (float)movementTotalSteps / (float)yAbsTotalSteps;
		float yScaledMaxSpeed = xyzStage->YAxis.MaxSpeed * invYScaled;
		movementMaxSpeed = (yScaledMaxSpeed < movementMaxSpeed) ? yScaledMaxSpeed : movementMaxSpeed;
		float yScaledAcceleration = xyzStage->YAxis.MaxAcceleration * invYScaled;
		movementAcceleration = (yScaledAcceleration < movementAcceleration) ? yScaledAcceleration : movementAcceleration;

		//If the Y actuator has the leading stepper...
		if (movement->LeadingStepsTotal == yAbsTotalSteps)
		{
			float yScaled = (float)yAbsTotalSteps / (float)movementTotalSteps;
			leadingAcceleration = movementAcceleration * yScaled;
			leadingMaxSpeed = movementMaxSpeed * yScaled;
			leadingEntrySpeed = movement->MovementEntrySpeed * yScaled;
			leadingExitSpeed = movementExitSpeed * yScaled;
		}
	}
	if (zSteps != 0)
	{
		float invZScaled = (float)movementTotalSteps / (float)zAbsTotalSteps;
		float zScaledMaxSpeed = xyzStage->ZAxis.MaxSpeed * invZScaled;
		movementMaxSpeed = (zScaledMaxSpeed < movementMaxSpeed) ? zScaledMaxSpeed : movementMaxSpeed;
		float zScaledAcceleration = xyzStage->ZAxis.MaxAcceleration * invZScaled;
		movementAcceleration = (zScaledAcceleration < movementAcceleration) ? zScaledAcceleration : movementAcceleration;

		//If the Z actuator has the leading stepper...
		if (movement->LeadingStepsTotal == zAbsTotalSteps)
		{			
			float zScaled = (float)zAbsTotalSteps / (float)movementTotalSteps;
			leadingAcceleration = movementAcceleration * zScaled;
			leadingMaxSpeed = movementMaxSpeed * zScaled;
			leadingEntrySpeed = movement->MovementEntrySpeed * zScaled;
			leadingExitSpeed = movementExitSpeed * zScaled;
		}
	}
	if (eSteps != 0)
	{
		float invEScaled = (float)movementTotalSteps / (float)eAbsTotalSteps;
		float eScaledMaxSpeed = motorPrinthead->MaxSpeed * invEScaled;
		movementMaxSpeed = (eScaledMaxSpeed < movementMaxSpeed) ? eScaledMaxSpeed : movementMaxSpeed;
		float eScaledAcceleration = motorPrinthead->MaxAcceleration * invEScaled;
		movementAcceleration = (eScaledAcceleration < movementAcceleration) ? eScaledAcceleration : movementAcceleration;

		//If the E actuator has the leading stepper...
		if (movement->LeadingStepsTotal == eAbsTotalSteps)
		{
			float eScaled = (float)eAbsTotalSteps / (float)movementTotalSteps;
			leadingAcceleration = movementAcceleration * eScaled;
			leadingMaxSpeed = movementMaxSpeed * eScaled;
			leadingEntrySpeed = movement->MovementEntrySpeed * eScaled;
			leadingExitSpeed = movementExitSpeed * eScaled;
		}
	}

	//StepPulseDelay is in units of cycles.
	//StepPulseDuration is in units of microseconds.
	//Timer 0 with a prescaler of 8 and a CPU frequency of 16 MHz will tick once every 0.5 microseconds.
	movement->StepPulseDelay = 2 * stepPulseDuration;

	//Number of steps to go from entry speed to the maximum allowable exit speed assuming pure acceleration/deceleration throughout the entire movement.
	float leadingEntryToExitSteps = fabs((leadingExitSpeed - leadingEntrySpeed) / leadingAcceleration) * (leadingEntrySpeed + 0.5 * (leadingExitSpeed - leadingEntrySpeed));
	//Number of steps for the leading stepper to go from entry speed to maximum speed, then from maximum speed to exit speed.
	float leadingEntryToCruiseSteps = ((leadingMaxSpeed - leadingEntrySpeed) / leadingAcceleration) * (leadingEntrySpeed + 0.5 * (leadingMaxSpeed - leadingEntrySpeed));
	//Number of steps required to decelerate from max speed to exit speed.
	float leadingCruiseToExitSteps = (leadingMaxSpeed != leadingExitSpeed) ? ((leadingMaxSpeed - leadingExitSpeed) / leadingAcceleration * (leadingExitSpeed + 0.5 * (leadingMaxSpeed - leadingExitSpeed))) : 0;
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

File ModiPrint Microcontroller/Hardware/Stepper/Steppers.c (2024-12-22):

#include "ModiPrintMicro.h"

stepper_realtime_t StepperRealTime;

//How acceleration is calculated:
//The acceleration formula estimates velocity with v_n = cycles_total_(n-1) * a.
//This velocity is estimated with a time value of the previous step to avoid square roots.
//The number of cycles in between steps is estimated with cycles_n = 1 / v_n.
//Cycles is not calculated in a more conventional way ((v_n - v_(n-1)) / a) because that yields cycle values of zero considering previous estimations.
//Therefore, cycles are estimated with 1 / v_n, which introduces negligible error past the first estimated cycle which can be easily by initializing values with alternate equations.
//Note that the error will increase with higher accelerations.
//But reasonable movement parameters will yield a few % error at most where error decreases with increasing steps.
//Because error decreases with increasing steps, the cycles total value is kept across movements.
//These janky but simple calculations create an almost linear acceleration curve with only a single float divide per OCR1A value.
//The goal is to enable this program to perform all acceleration calculations on demand without the limitation of buffers to hold these values.
//Note these values are sometimes not even close to the actual values they represent.
//Yet, these values usually calculate a OCR1A value close enough to the real thing.

//The total cycles estimate.
//This value is incremented and decremented throughout the acceleration calculations of the movement.
//This value is remembered to circumvent initial errors in the acceleration calculations of the next movement.
//DEBUGTEMP as signed to check for negative values.
float VirtualTotalCycles;

//Flagged by Timer 1 when Timer 1 is running.
//Flagged false once a step has been executed.
//Prevents Timer 1 from triggering itself.
volatile uint8_t IsStepping = FALSE;
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
